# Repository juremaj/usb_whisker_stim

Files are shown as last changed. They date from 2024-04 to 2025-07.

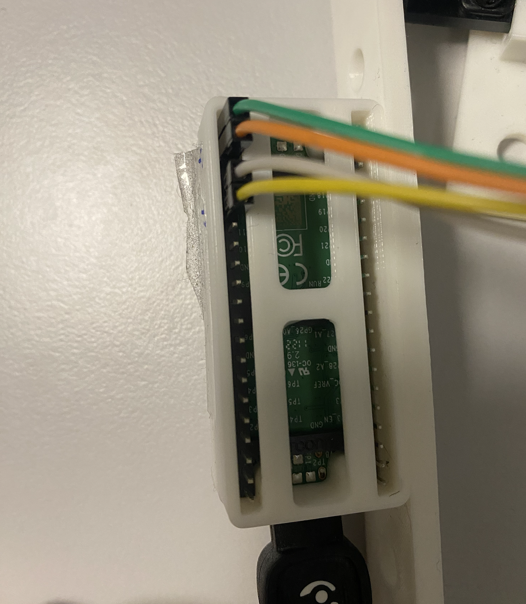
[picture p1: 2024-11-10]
resources/pics_stepper/pico_offrig.png

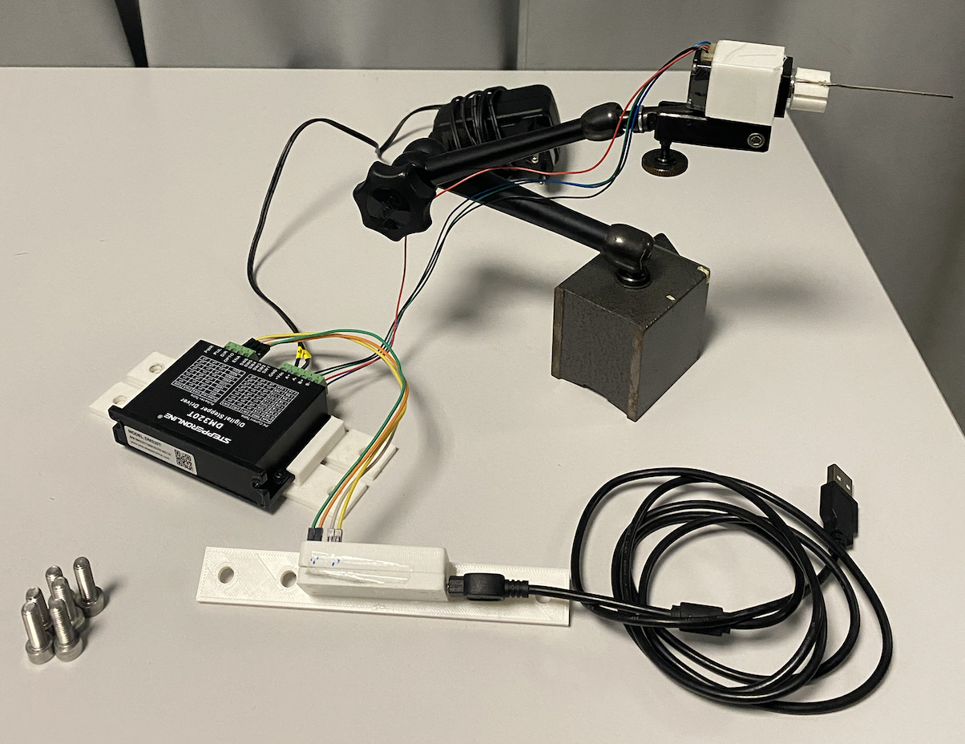
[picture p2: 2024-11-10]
resources/pics_stepper/all_offrig_1.png

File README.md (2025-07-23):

# usb_whisker_stim
Simple USB device for whisker stimulation

## Hardware
### Components list:
- [Raspberry Pico](https://www.raspberrypi.com/products/raspberry-pi-pico/) 
- [Stepper motor](https://www.omc-stepperonline.com/fr/nema-8-bipolaire-1-8deg-4ncm-5-7oz-in-0-6a-6v-20x20x38mm-4-fils-8hs15-0604s?srsltid=AfmBOopk5yiqgoLouQ6k0vKjGUFTYhUCFirBDUTsyYDL8u_syfw4GUZw) (Nema 8 Bipolar 1.8deg 4Ncm(5.7oz.in) 0.6A 20x20x38mm 4 Wires model: 8HS15-0604S)
- [Driver](https://www.omc-stepperonline.com/fr/pilote-numerique-pas-a-pas-0-3-2-2a-10-30vdc-pour-nema-8-11-14-16-17-moteur-pas-a-pas-dm320t?srsltid=AfmBOor4CZzB0a09o4nP59VcgGCvBjCYBjOBE6GV5xBhgGucQqpYNq2G) (Digital Stepper Driver 0.3-2.2A 10-30VDC for Nema 8, 11, 14, 16, 17 Stepper Motor, model: DM320T)
- Articulated arm

### Setup:
- For instruction on how to wire up the device see the pictures in `resources/pics_stepper`
- This involves three simple steps:
    1) connecting 4 motor pins to the motor driver
    2) connecting +/- of 12 V power adapter to motor driver
    3) connecting 4 pico pins to the motor driver
- Then the final step is to configure the stepper settings (current and number of steps per revolution) - see the table on the driver and `driver_settings.png` for the default setting (DOWN DOWN DOWN DOWN DOWN UP DOWN)

## Raspberry Pico code
- All code to be uploaded to raspberry pico is available in `pico_whisker_stim`.
- To see how to put the code to the raspberry pico you can follow the steps here: https://projects.raspberrypi.org/en/projects/getting-started-with-the-pico/5 
- Most important steps:
    - Set up a way to control the pico from your computer (Thonny IDE in this case)
    - Add micropython firmware to the board
    - Test if everything works ('blink' onboard LED)
    - Check the intructions on how to upload a script
    - The only thing that needs to be uploaded is the `usb_whisker_stim/main.py` script

## Demo
- Once you have followed the instructions above you can test if the motor works
- The code `trigger_stim.py` is an example of how the device can be used to randomly deliver one of the 2 pre-programmed stimuli
- To run that code you will need to `pip install pyserial` and `pip install numpy` - ideally in a virtual environment such as conda
- The only thing that needs to be changed is line 7 to tell the script where it can find the pico (this will depend on the OS and to which port the pico gets connected) 
- This would usually be done by another script running the experimental protocol (for example the camera synchronisation scripts in `control_exp`)

## 3D printing

- The 3d printed parts are optional, mostly as adapters (for example to screw the parts into a thorlabs optics breadboard and to relay the rotation of the stepper to a rod for whisker stim) - but these can easily be replaced by other parts
- All parts are available in `resources/3dprint_stepper` and under `resources/links.md` there is also a link to an external case also available here: [Raspberry Pico Case](https://www.thingiverse.com/thing:4737733)

## 'backup' folders
These contain older version of code and resources - these can be ignored.

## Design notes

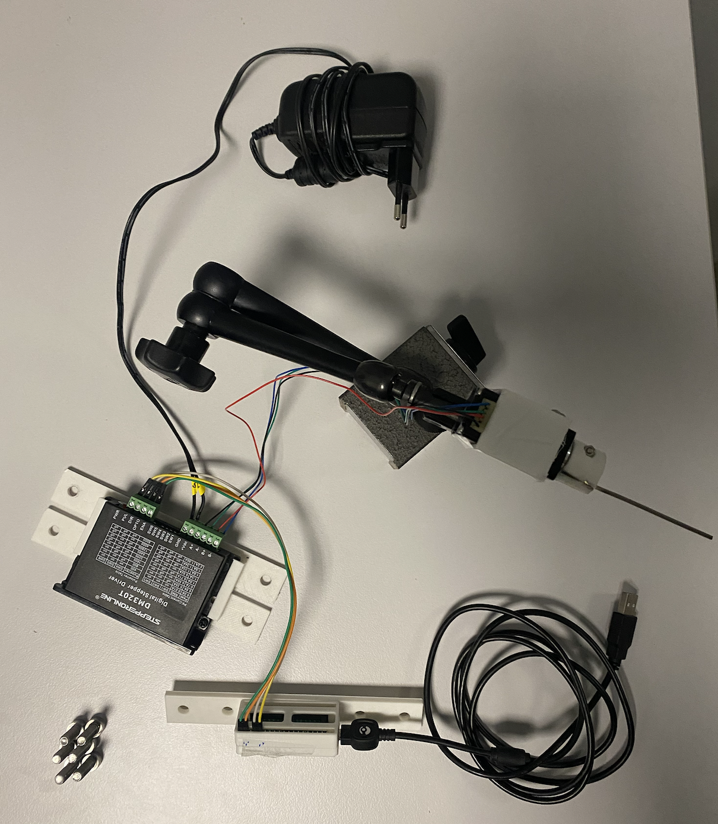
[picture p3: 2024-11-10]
resources/pics_stepper/all_offrig_2.png

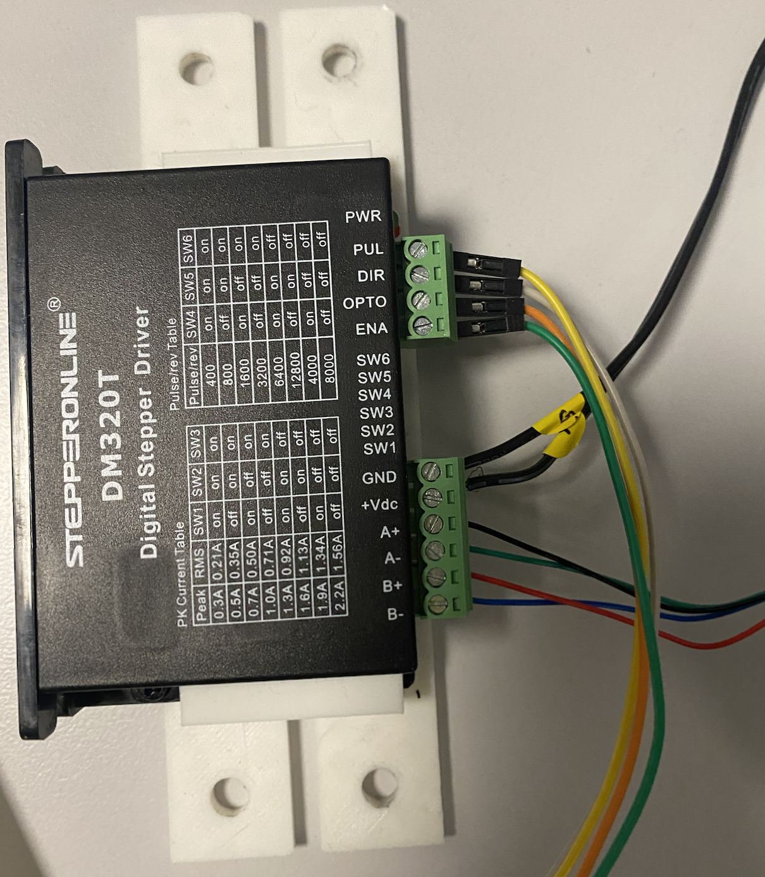
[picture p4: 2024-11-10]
resources/pics_stepper/driver_offrig.png

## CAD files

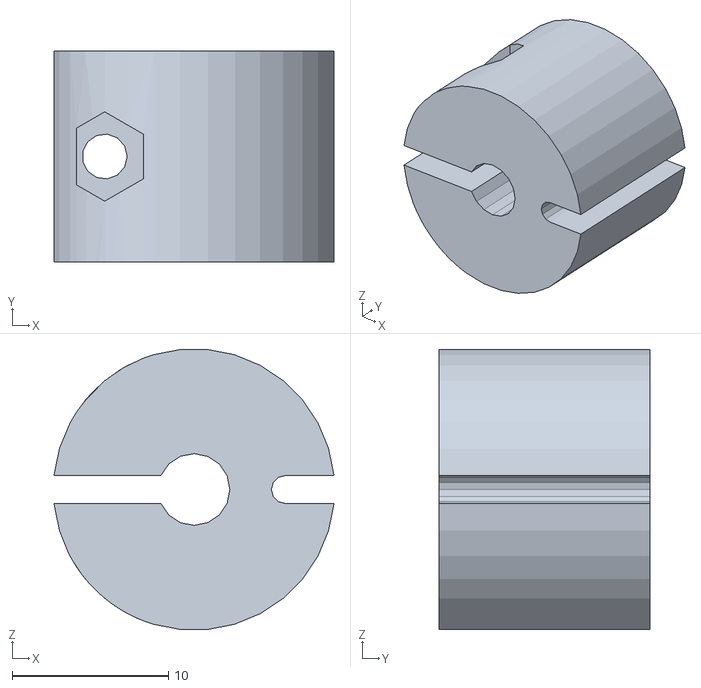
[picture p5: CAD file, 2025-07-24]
resources/3dprint_stepper/motor_to_actuator_adapter.stl
17.9 x 13.5 x 17.9

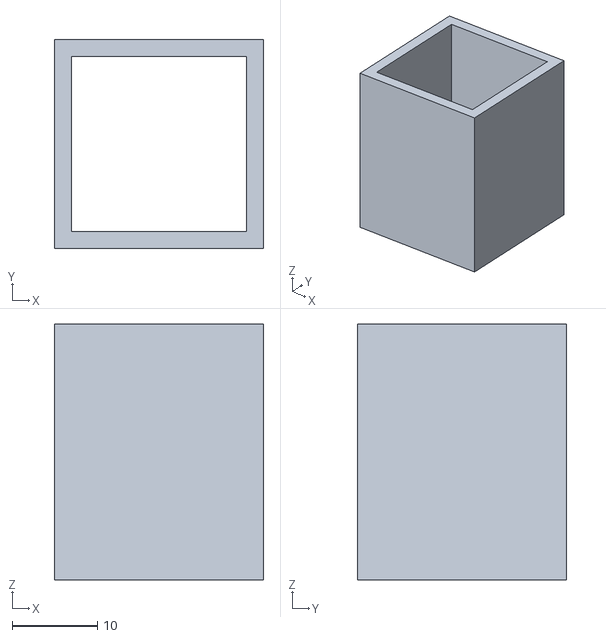
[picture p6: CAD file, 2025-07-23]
resources/3dprint_stepper/motor_case.stl
24.5 x 24.5 x 30.0

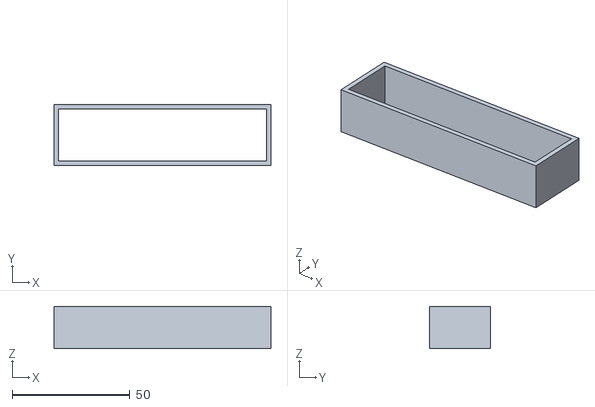
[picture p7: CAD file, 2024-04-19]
resources/3dprint_stepper/motor_driver_casing_mid.stl
92.0 x 26.0 x 18.0

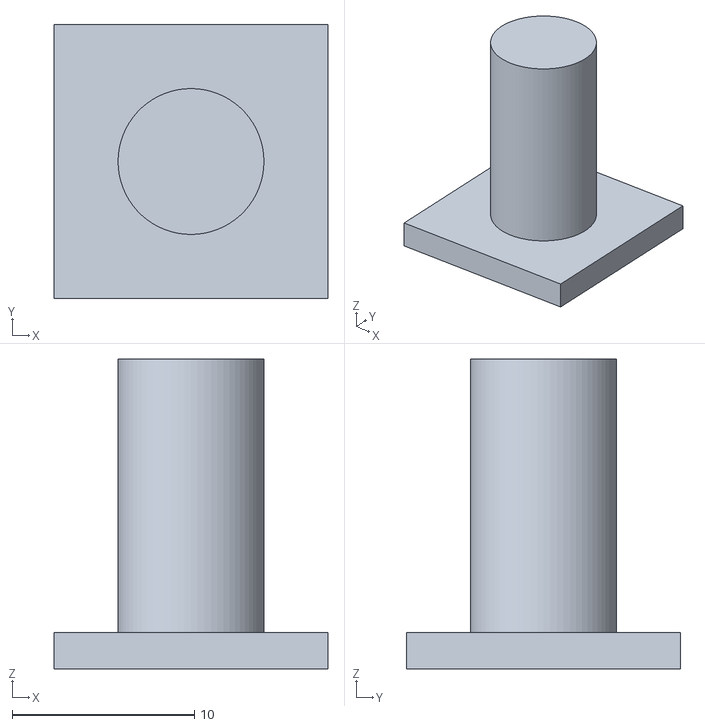
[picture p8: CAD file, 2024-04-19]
resources/3dprint_stepper/arm_to_motor_adapter.stl
15.0 x 15.0 x 17.0

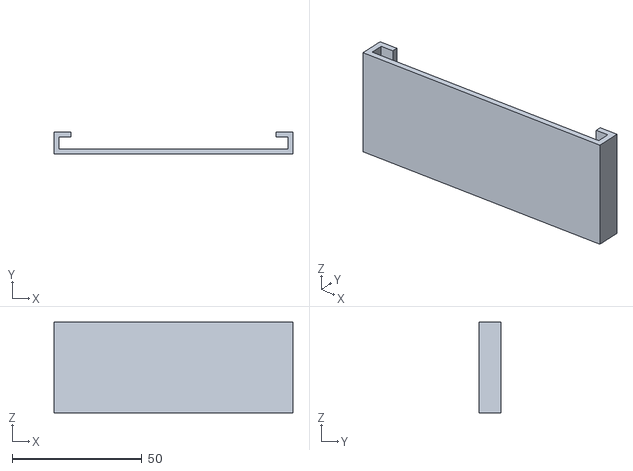
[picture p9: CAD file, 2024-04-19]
resources/3dprint_stepper/motor_driver_casing_back.stl
92.0 x 8.50 x 35.0

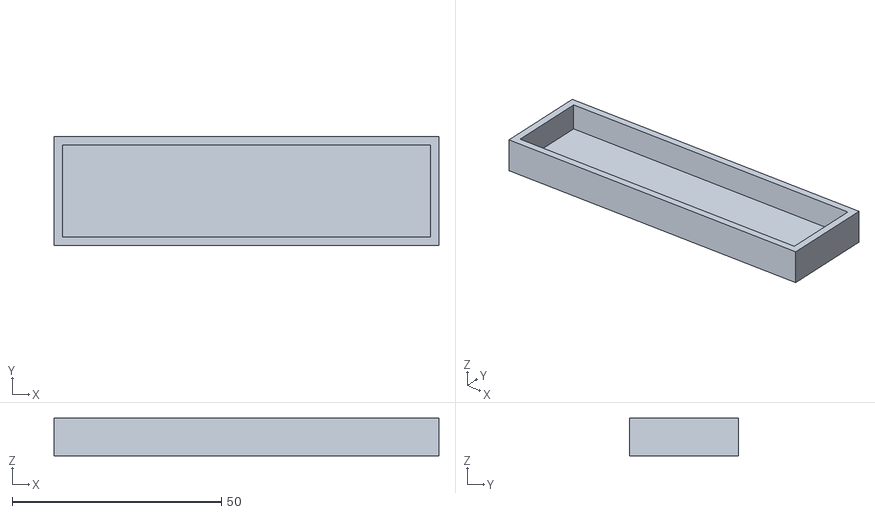
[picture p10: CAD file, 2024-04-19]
resources/3dprint_stepper/motor_driver_casing_front.stl
92.0 x 26.0 x 9.00

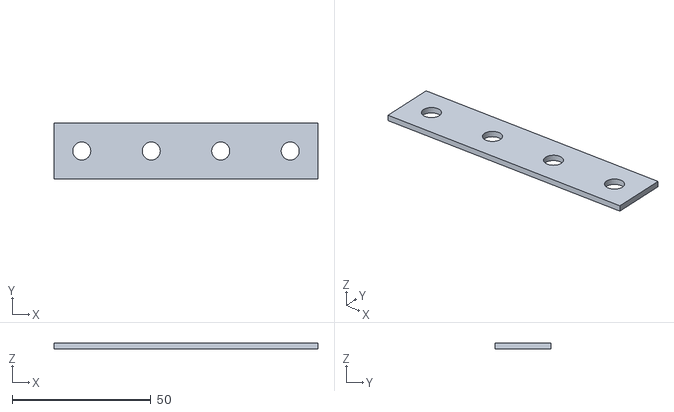
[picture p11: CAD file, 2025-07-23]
resources/3dprint_stepper/thorlabs_board_adapter_4x1.stl
95.0 x 20.0 x 2.00

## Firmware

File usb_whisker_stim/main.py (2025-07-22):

import sys

from machine import Pin
import utime
import time


def stim0(dir, pul, n_steps_pos=1600, n_steps_stim = 400, n_stim_rep=4, isi=0.0009):
    dir.value(1) # direction of spin (only difference between stimuli)

    for i in range(n_steps_pos):
        pul.value(1)
        utime.sleep_us(isi)
        pul.value(0)
        utime.sleep_us(isi)

    # start measuring time
    start_time = utime.ticks_ms()
    for i in range(n_stim_rep*2):
        dir.value((i+1) % 2)  # alternate direction for each repetition
        for j in range(n_steps_stim):
            pul.value(1)
            utime.sleep_us(isi)
            pul.value(0)
            utime.sleep_us(isi)
    end_time = utime.ticks_ms()
    elapsed_time = utime.ticks_diff(end_time, start_time)
    print(f"Elapsed time for stimulus: {elapsed_time} ms")
    dir.value(0)

    for i in range(n_steps_pos):
        pul.value(1)
        utime.sleep_us(isi)
        pul.value(0)
        utime.sleep_us(isi)

# n_steps = 1600 # number of steps (set depending on hardware setting)
n_steps_pos = 300
n_steps_stim = 500 # 500 # number of steps for the stimulus
n_stim_rep = 5 # number of repetitions of the stimulus
isi = 185 # 185 # how fast to rotate

# blink led to show connection
pin = Pin("LED", Pin.OUT)

# blink three times to show it is connected
for i in range(6):
    pin.toggle()
    time.sleep(0.2)

# define pins to interface with the stepper motor driver
pul = Pin(12, Pin.OUT)
dir = Pin(13, Pin.OUT)
opto = Pin(14, Pin.OUT)
ena = Pin(15, Pin.OUT)

pul.value(0)# initialize the pulse and direction pins to low
dir.value(0) # -II-
ena.value(0) # dont yet enable the motor driver
opto.value(1) # set opto to up (this should be 3.3V reference, see answer here: https://stackoverflow.com/questions/62056411/stepper-motor-control-with-dm320t-raspberry-pi-3b-and-matlab)

time.sleep(1)

# now wait for the command to trigger the stim
# (the command arrives via usb serial)

while True:
    ena.value(1)
    try:
        command = sys.stdin.readline().strip()
        
        print(f"Triggering stim: {command}")
        
        if command.lower() == "0":
            # stim0(dir, pul, n_steps, isi)
            stim0(dir, pul, n_steps_pos=n_steps_pos, n_steps_stim=n_steps_stim, n_stim_rep=n_stim_rep, isi=isi)
            print('TAC')


        else:
            # quick blink if command not recognized
            for i in range(10):
                pin.toggle()
                time.sleep(0.1)

    except KeyboardInterrupt:

        pul.value(0)
        dir.value(0)
        opto.value(0)
        ena.value(0)

        break

# disable the driver
pul.value(0)
dir.value(0)
opto.value(0)
ena.value(0)

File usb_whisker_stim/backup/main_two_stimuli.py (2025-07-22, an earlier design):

import sys

from machine import Pin
import utime
import time

import random

def stim2(dir, pul, n_steps=16000, n_steps_change=1000, isi=0.0009):

    # change direction after random number of steps:
    print("new stim2")
    # randomly choose n_steps_change to be between 10 and 100
    n_steps_change = random.randint(10, 100)

    count = 0 
    for i in range(n_steps):
        # randomly choose duration of this step between 0.01 and 0.001

        # randomly sample direction every n_steps_change steps
        if count == n_steps_change:
            print("nwwww")
            dir.value(random.choice([0, 1]))
            isi = random.uniform(0.001, 0.01)
            # multiply n_steps_change by 1 if its close to 0.01 and by 10 if it is close to 0.001
            n_steps_change = random.randint(10, int(1/isi))
            count = 0

        count+=1

        pul.value(1)
        time.sleep(isi)
        pul.value(0)
        time.sleep(isi)


def stim0(dir, pul, n_steps=1600, isi=0.0009):
    dir.value(0) # direction of spin (only difference between stimuli)

    for i in range(n_steps):
        pul.value(1)
        utime.sleep_us(isi)
        pul.value(0)
        utime.sleep_us(isi)

def stim1(dir, pul, n_steps=1600, isi=0.0009):
    dir.value(1) # direction of spin (only difference between stimuli)

    for i in range(n_steps):
        pul.value(1)
        time.sleep(isi)
        pul.value(0)
        time.sleep(isi)


n_steps = 400 # number of steps (set depending on hardware setting)
isi = 1000 # how fast to rotate 

# blink led to shwo connection
pin = Pin("LED", Pin.OUT)

# blink three times to show it is connected
for i in range(6):
    pin.toggle()
    time.sleep(0.2)

# define pins to interface with the stepper motor driver
pul = Pin(12, Pin.OUT)
dir = Pin(13, Pin.OUT)
opto = Pin(14, Pin.OUT)
ena = Pin(15, Pin.OUT)

pul.value(0)# initialize the pulse and direction pins to low
dir.value(0) # -II-
ena.value(0) # dont yet enable the motor driver
opto.value(1) # set opto to up (this should be 3.3V reference, see answer here: https://stackoverflow.com/questions/62056411/stepper-motor-control-with-dm320t-raspberry-pi-3b-and-matlab)

time.sleep(1)

# now wait for the command to trigger the stim
# (the command arrives via usb serial)

while True:
    try:
        command = sys.stdin.readline().strip()
        
        print(f"Triggering stim: {command}")

        if command.lower() == "0":
            ena.value(1)
            stim0(dir, pul, n_steps, isi)
            print('TAC')
            ena.value(0)



        elif command.lower() == "1":
            stim1(dir, pul, n_steps=n_steps, isi=isi)
        
        elif command.lower() == "2":
            stim2(dir, pul, n_steps=160000, n_steps_change=100, isi=0.001)

        else:
            # quick blink if command not recognized
            for i in range(10):
                pin.toggle()
                time.sleep(0.1)

    except KeyboardInterrupt:

        pul.value(0)
        dir.value(0)
        opto.value(0)
        ena.value(1)

        break

# disable the driver
pul.value(0)
dir.value(0)
opto.value(0)
ena.value(0)

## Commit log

2024-01-09 first commit (first version)
    [servo_holder_v4.stl]
2024-04-11 some updates (for basic stepper etc.)
2024-04-11 first commit of new stepper hardware
2024-04-19 centuri meeting push
    [arm_to_motor_adapter.stl, motor_driver_casing_back.stl, motor_driver_casing_front.stl, motor_driver_casing_mid.stl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]
2024-11-10 final stepper version
2025-07-22 stepper final version
    [servo_holder_v4.stl]
2025-07-23 added missing 3d printed parts and articlated holder
    [motor_case.stl, thorlabs_board_adapter_4x1.stl]
2025-07-24 added 3d print for motor to actuator adapter
    [motor_to_actuator_adapter.stl]
